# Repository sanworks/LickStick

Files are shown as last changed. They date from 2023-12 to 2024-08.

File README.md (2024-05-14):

# LickStick
A capacitive lick sensing device designed for Neuroscience research.

## Important Note ##
LickStick is in beta testing, and may still have unresolved issues.

## Contents ##
This repository includes:
* Circuit board and enclosure design files
* Link to Bill of Materials
* Firmware (Arduino language, requires Teensy board package)
* A MATLAB class to control the LickStick device

## Setup ##
* Add /LickStick/MATLAB/ to the MATLAB path
* Connect a LickStick device to your PC
* See comments in LickStick.m for usage

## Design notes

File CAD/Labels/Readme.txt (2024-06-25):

*** Screw Terminal Label Instructions ***

---Materials---
Printer: Brother PT-P900W
Label tape: TZe-S135 (12mm/0.47", White on clear, strong adhesive)

---Print settings---
Print resolution: Standard
Output: Standard
Options: Half Cut, Output Directly to Printer Driver. ALL OTHERS UNCHECKED

---Instructions---
Print labels
Cut to size on dotted lines, excluding the lines.
Peel and stick on label space above wire entry holes on wire terminal block.

*** Lickstick Logo Decal Instructions ***
Print with a die-cut sticker service.
Recommended vendor: Jukebox Print, https://www.jukeboxprint.com/ select Permanent Matte finish.

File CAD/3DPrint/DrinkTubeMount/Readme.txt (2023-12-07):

Drink tube mount designs.
v0.1 is very experimental! No results guaranteed!

Designs optimized for 3D printing.
Use FDM, with 0.4mm nozzle (e.g. Ultimaker 2+)

The mount holds a 15Ga hypodermic drink tube in place by press fit. 
The DirectContact version presses a 22ga wire onto the tube.
The FieldCoupling version places the wire adjacent to the tube with an insulating layer of plastic blocking current flow.
The mounts have a socket for a captured 4-40 nut, McMaster Part# 90730A005

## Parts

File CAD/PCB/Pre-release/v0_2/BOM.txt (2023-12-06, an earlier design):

https://docs.google.com/spreadsheets/d/1yjmNU1V_IxbT4ZvGDEUfZIvdB87yUdJNFsId-nouO-U/edit?usp=sharing

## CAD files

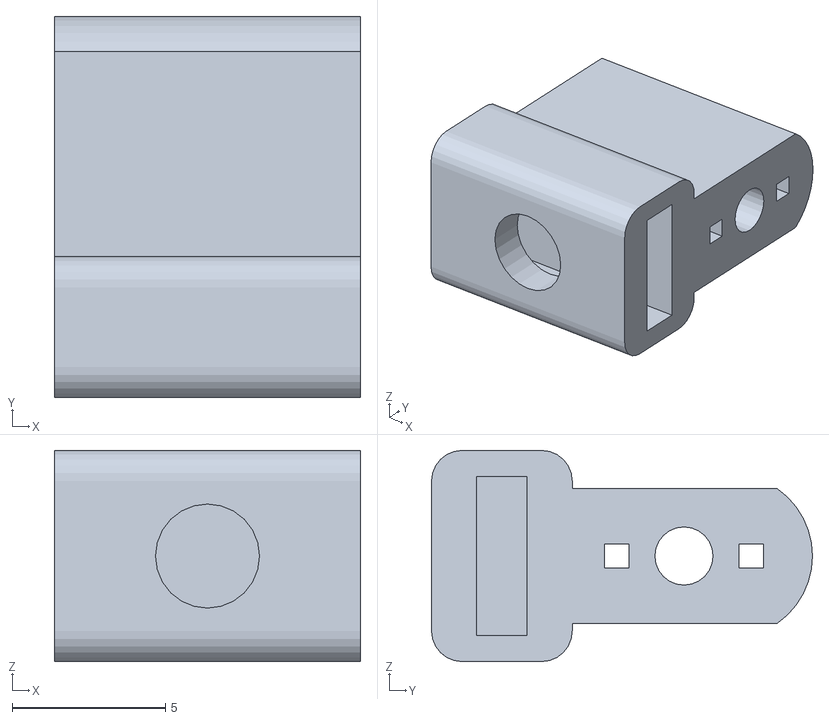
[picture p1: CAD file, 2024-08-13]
CAD/3DPrint/DrinkTubeMount/STL/LickStick_Mount_v0_2_FieldCoupling.stl
10.0 x 12.5 x 6.90

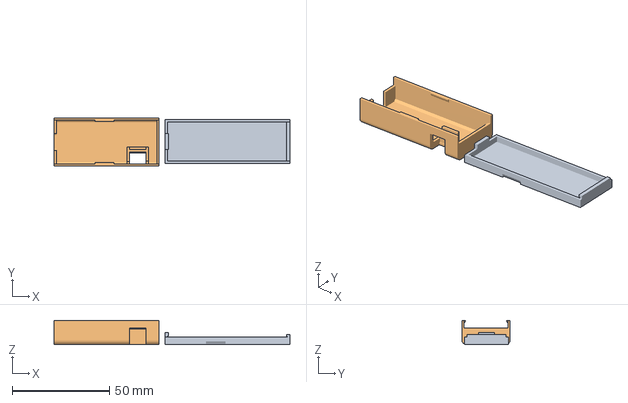
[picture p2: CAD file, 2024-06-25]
CAD/3DPrint/Enclosure/LickStick0_3_4.3mf
121.4 x 24.9 x 12.6 mm
LickStick_Enclosure_1_0_0_Bottom.stl
LickStick_Enclosure_1_0_0_Top.stl

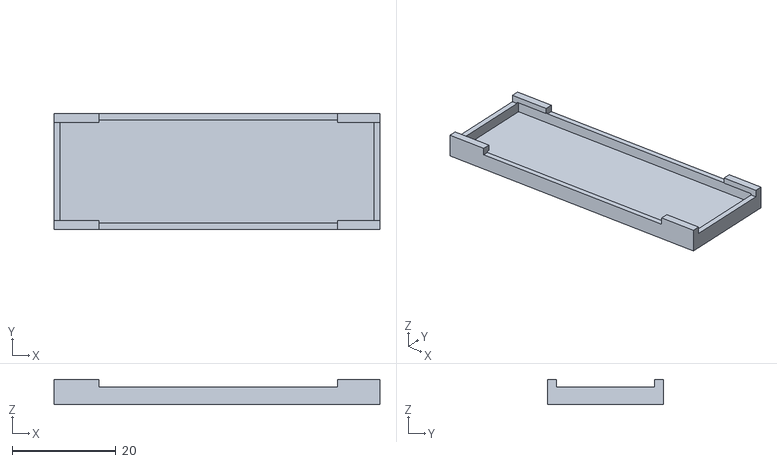
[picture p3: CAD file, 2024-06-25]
CAD/3DPrint/Enclosure/Pre-release/LickStick0_3.stl
62.8 x 22.3 x 4.85

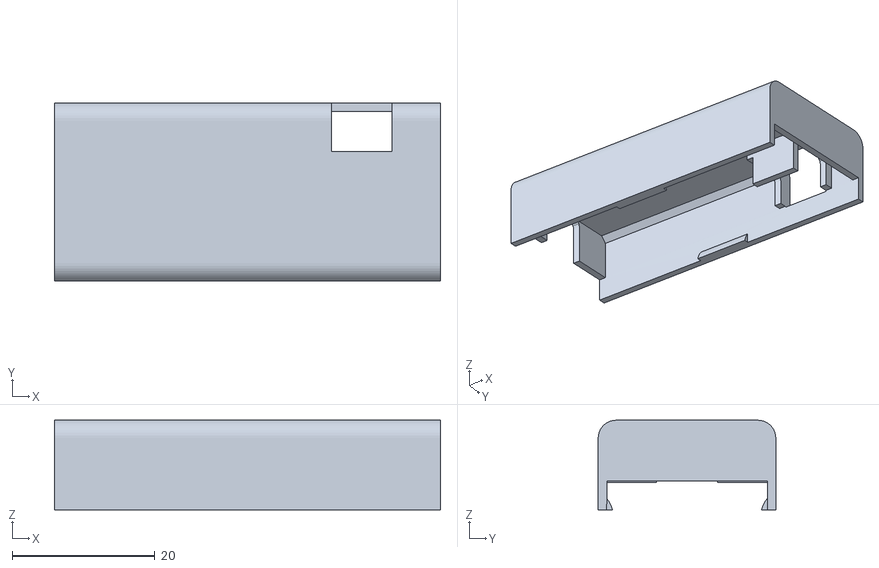
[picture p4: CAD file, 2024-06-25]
CAD/3DPrint/Enclosure/STL/LickStick_Enclosure_Top_1_0_0.stl
54.1 x 24.9 x 12.6

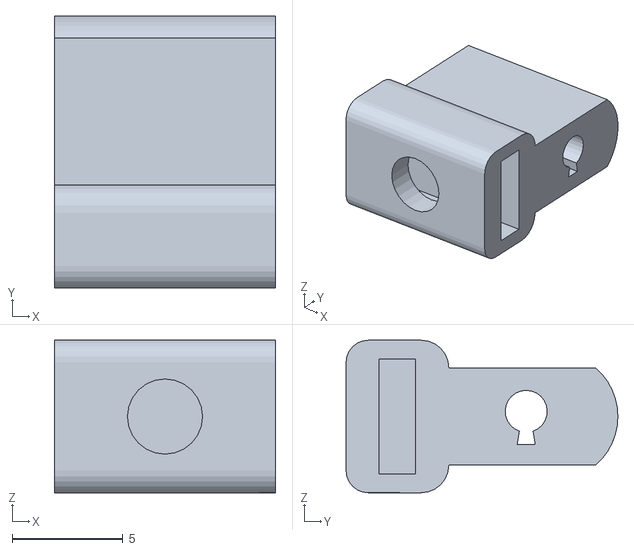
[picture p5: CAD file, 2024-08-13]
CAD/3DPrint/DrinkTubeMount/STL/LickStick_Mount_v0_2_DirectContact.stl
10.00 x 12.3 x 6.90

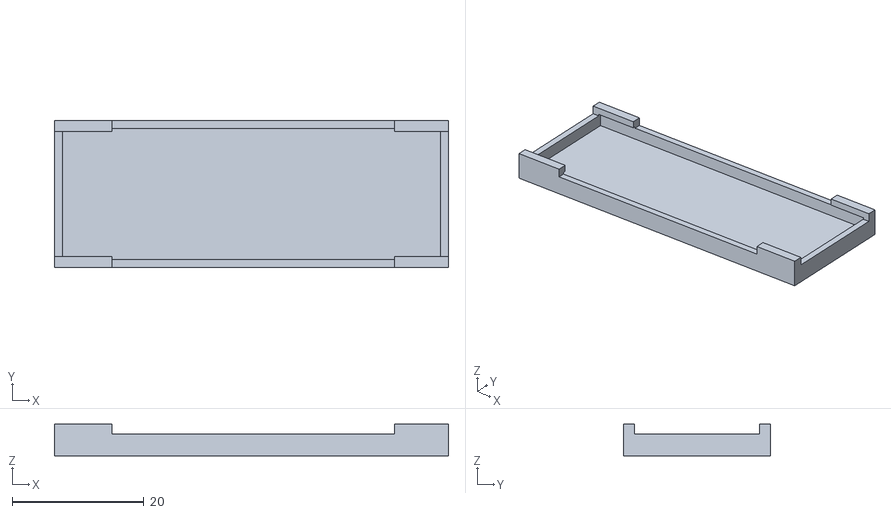
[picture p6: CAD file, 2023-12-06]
CAD/3DPrint/Enclosure/Pre-release/LickStick0_2.stl
59.8 x 22.3 x 4.85

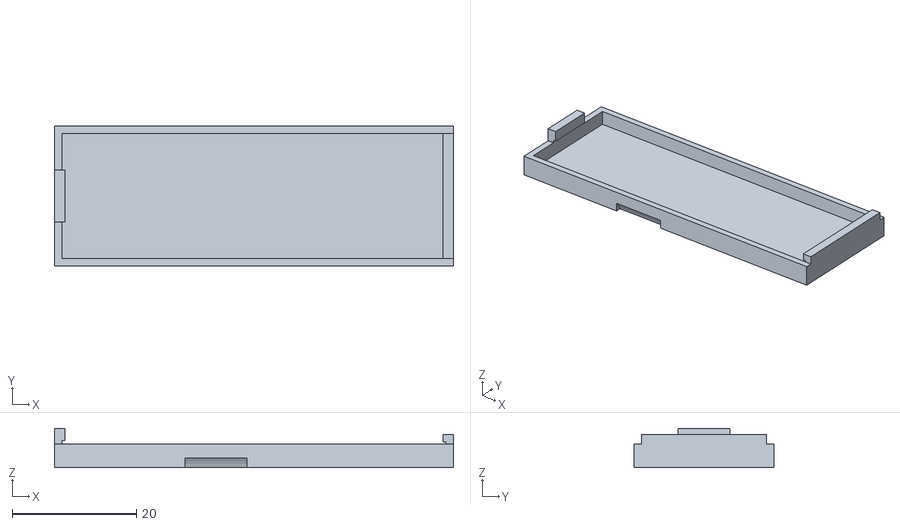
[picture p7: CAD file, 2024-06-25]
CAD/3DPrint/Enclosure/STL/LickStick_Enclosure_Bottom_1_0_0.stl
64.3 x 22.5 x 6.35

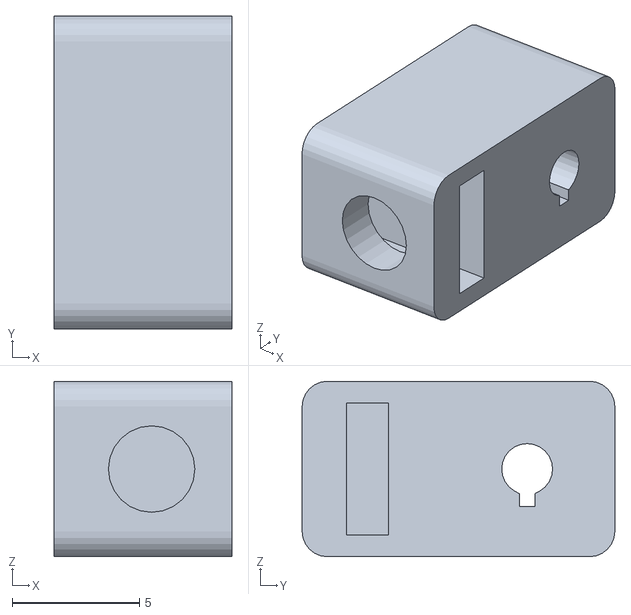
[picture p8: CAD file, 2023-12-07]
CAD/3DPrint/DrinkTubeMount/STL/LickStick_Mount_v0_1_DirectContact.stl
7.00 x 12.3 x 6.90

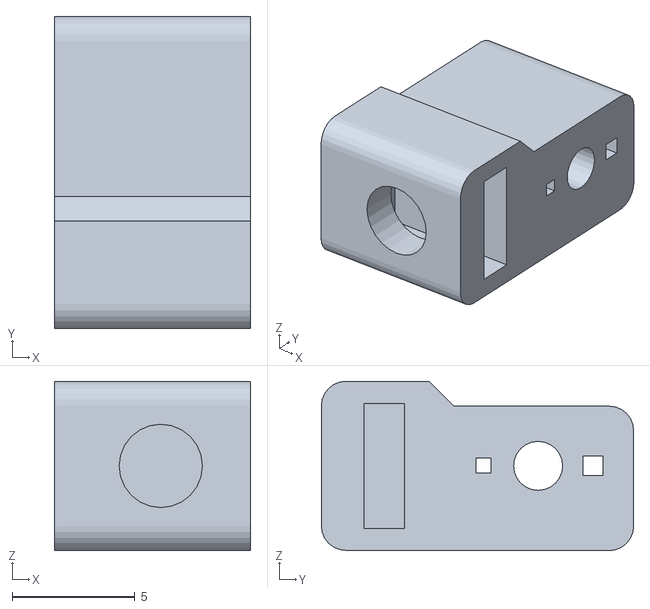
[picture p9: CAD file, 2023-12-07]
CAD/3DPrint/DrinkTubeMount/STL/LickStick_Mount_v0_1_FieldCoupling.stl
8.00 x 12.8 x 6.91

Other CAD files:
CAD/3DPrint/DrinkTubeMount/LickStick_Mount_v0_1.skp
CAD/3DPrint/DrinkTubeMount/LickStick_Mount_v0_2.skp
CAD/3DPrint/Enclosure/LickStick_Enclosure_1_0_0.skp
CAD/3DPrint/Enclosure/Pre-release/LickStick0_2.skp
CAD/3DPrint/Enclosure/Pre-release/LickStick0_3.skp
CAD/3DPrint/Enclosure/Pre-release/LickStick0_3_3.skp
CAD/3DPrint/Enclosure/Pre-release/LickStick0_3_4.skp

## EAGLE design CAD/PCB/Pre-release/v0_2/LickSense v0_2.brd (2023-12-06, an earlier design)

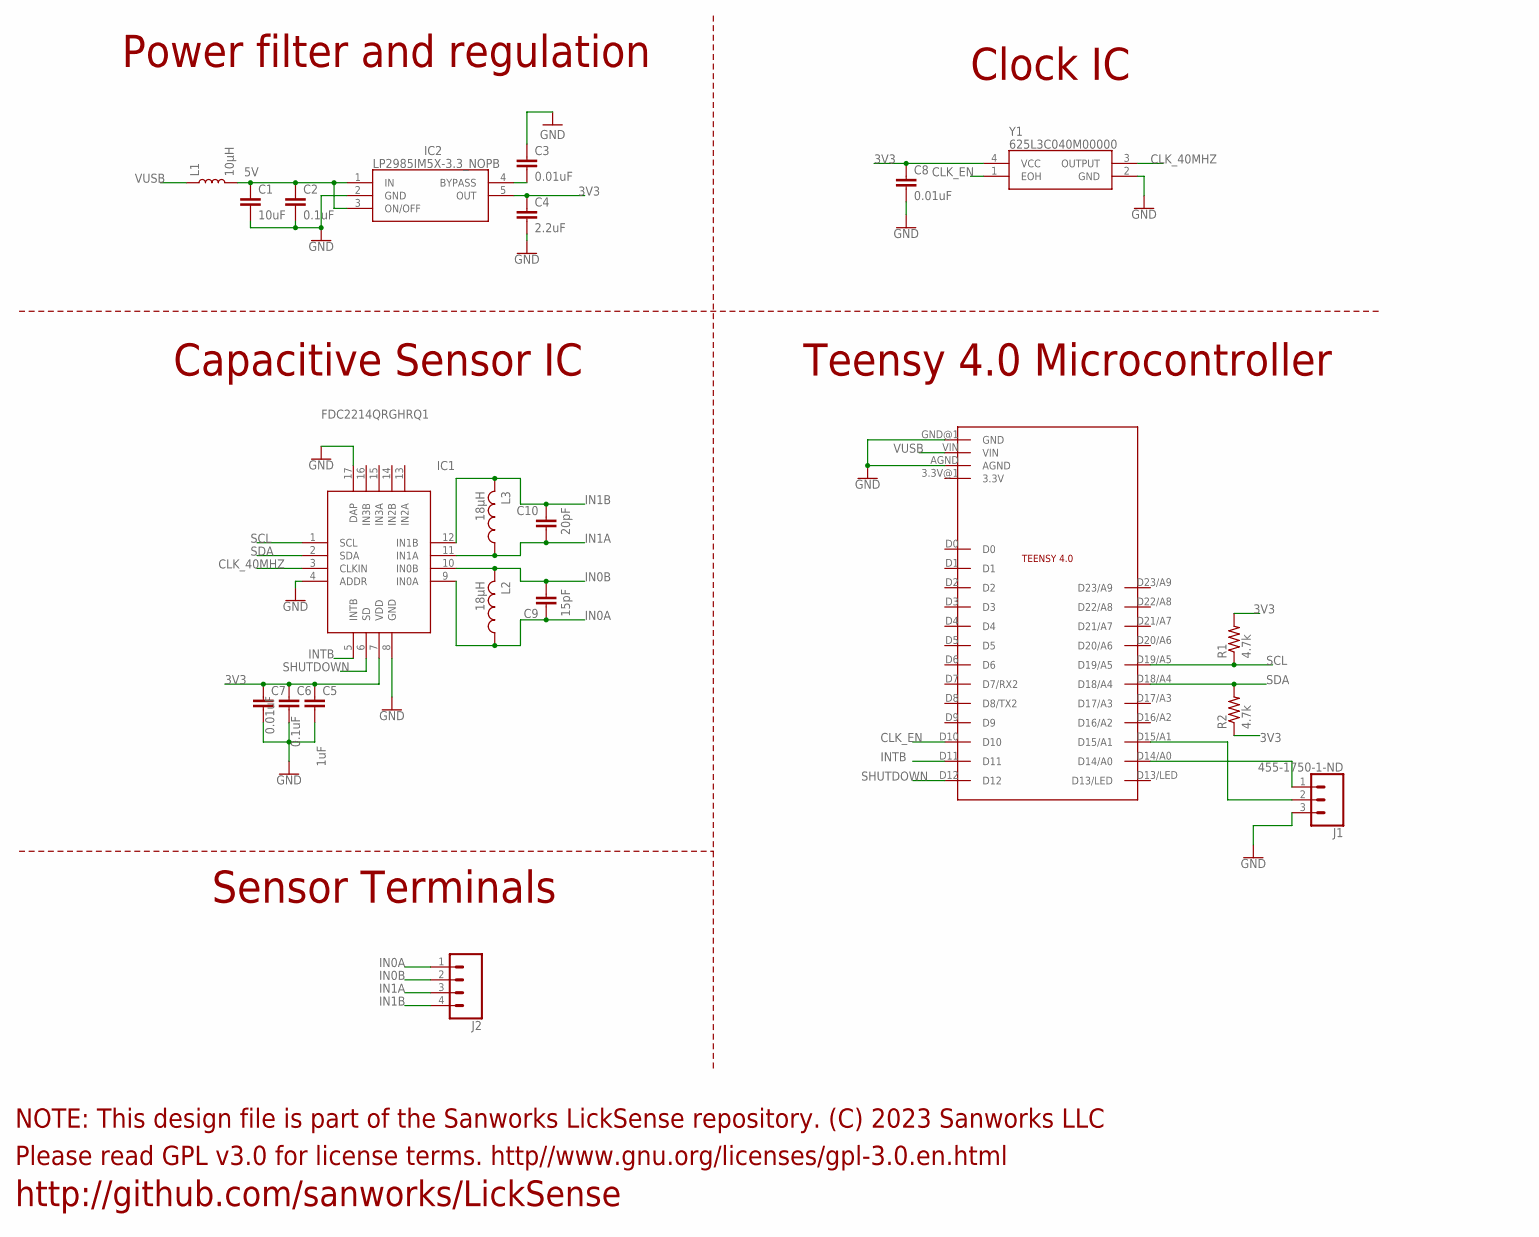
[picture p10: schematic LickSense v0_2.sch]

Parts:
C1: 10uF; 0805
C2, C6: 0.1uF; 0805
C3, C7, C8: 0.01uF; 0805
C4: 2.2uF; 0805
C5: 1uF; 0805
C9: 15pF; 0805
C10: 20pF; 0805
IC1: FDC2214QRGHRQ1; QFN50P400X400X80-17N
IC2: LP2985IM5X-3.3_NOPB; SOT95P280X145-5N
J1: 455-1750-1-ND; 1X03
J2: CONN_04PTH; 1X04
L1: 10μH; 0806
L2, L3: 18μH; L3225P
MC1: TEENSY4.0_SIMPLE_NO_VUSB
R1, R2: 4.7k; R0805
Y1: 625L3C040M00000

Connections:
3V3: C4.1, C5.1, C6.1, C7.1, C8.1, IC1.7 (VDD), IC2.5 (OUT), R1.2, R2.1, Y1.4 (VCC)
5V: C1.1, C2.1, IC2.1 (IN), IC2.3 (ON/OFF), L1.2
CLK_40MHZ: IC1.3 (CLKIN), Y1.3 (OUTPUT)
CLK_EN: MC1.D10, Y1.1 (EOH)
DIO1: J1.1, MC1.D14/A0
DIO2: J1.2, MC1.D15/A1
GND: C1.2, C2.2, C3.1, C4.2, C5.2, C6.2, C7.2, C8.2, IC1.4 (ADDR), IC1.8 (GND), IC1.17 (DAP), IC2.2 (GND), J1.3, MC1.AGND, MC1.GND@1 (GND), Y1.2 (GND)
IN0A: C9.1, IC1.9 (IN0A), J2.1, L2.1
IN0B: C9.2, IC1.10 (IN0B), J2.2, L2.2
IN1A: C10.1, IC1.11 (IN1A), J2.3, L3.1
IN1B: C10.2, IC1.12 (IN1B), J2.4, L3.2
INTB: IC1.5 (INTB), MC1.D11
unnamed: C3.2, IC2.4 (BYPASS)
SCL: IC1.1 (SCL), MC1.D19/A5, R1.1
SDA: IC1.2 (SDA), MC1.D18/A4, R2.2
SHUTDOWN: IC1.6 (SD), MC1.D12
VUSB: L1.1, MC1.VIN

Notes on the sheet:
Teensy 4.0 Microcontroller
Clock IC
Power filter and regulation
Capacitive Sensor IC
Sensor Terminals
Please read GPL v3.0 for license terms. http//www.gnu.org/licenses/gpl-3.0.en.html
NOTE: This design file is part of the Sanworks LickSense repository. (C) 2023 Sanworks LLC
http://github.com/sanworks/LickSense

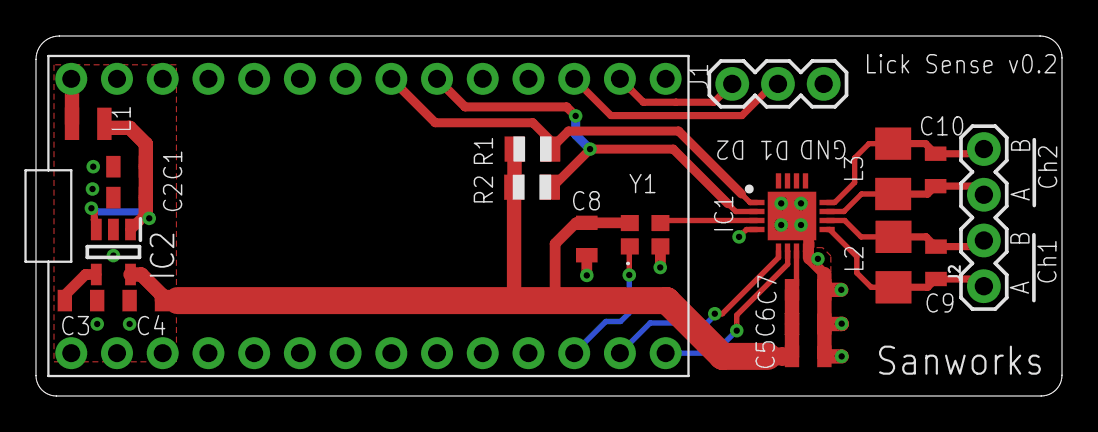
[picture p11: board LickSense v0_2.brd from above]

Board: 2 copper layers, 57.0 x 20.0 mm, 21 parts (0 on the bottom side), 17 nets.

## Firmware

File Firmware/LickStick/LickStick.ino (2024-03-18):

/*
  ----------------------------------------------------------------------------

  This file is part of the Sanworks LickSense repository
  Copyright (C) Sanworks LLC, Rochester, New York, USA

  ----------------------------------------------------------------------------

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
*/

#include <Wire.h>    // Arduino's builtin I2C class
#include "ArCOM.h"   // A wrapper to simplify transactions of different datatypes via USB serial
#include "FDC2214.h" // A class to interface with the Texas Instruments FDC2214 capacitive sensor IC

// Firmware version
#define FIRMWARE_VERSION 2

// Pin definitions
#define CLK_EN 10  // Clock enable
#define INTB 11    // Interrupt pin (configured below to report data ready)
#define SHTDWN 12  // Shutdown pin (used to reset device)
#define DIO1 15    // Digital I/O pin 1 (Middle position on green screw terminal header)
#define DIO2 14    // Digital I/O pin 2 (Right position on green screw terminal header)
#define LED_PIN 13 // LED

// Parameters
#define THRESH_DEFAULT 1900000 // Default touch detection threshold. Used from power-on until the PC connects.

// Setup interfaces
ArCOM USBCOM(Serial);
FDC2214 SensorIC(CLK_EN, INTB, SHTDWN);

// Timer used to read the sensor at even intervals
IntervalTimer readTimer;

// Program variables
byte opByte = 0;
byte inByte = 0;
byte usbStreaming = 0;
byte lickDetected = 0;
byte ledEnabled = 0;
uint16_t regValue = 0;
uint32_t thresholdValue = 0;
uint32_t nDebounceCycles = 20; // 20 cycles @ 2kHz sampling = 100Hz max licking
uint32_t debounceCounter = 0;
uint32_t nSamplesToReturn = 0;
union {
    uint8_t uint8[4];
    uint16_t uint16[2];
    uint32_t uint32[1];
} sensorValue;
union {
    byte byteArray[4];
    float floatVal;
} samplingInterval; // Hardware timer period in microseconds (500 = 2kHz). Set as a Union so it can be read as bytes.

void setup() {
  Wire.begin();
  SensorIC.init();
  pinMode(DIO1, OUTPUT);
  digitalWrite(DIO1, LOW);
  pinMode(DIO2, OUTPUT);
  digitalWrite(DIO2, LOW);
  pinMode(LED_PIN, OUTPUT);
  digitalWrite(LED_PIN, LOW);
  thresholdValue = THRESH_DEFAULT;
  samplingInterval.floatVal = 500;
  readTimer.begin(readCycle, samplingInterval.floatVal);
}

void loop() {
  if (USBCOM.available() > 0) {
    opByte = USBCOM.readByte();
    switch(opByte) {
      case 'F': // Return firmware version
        USBCOM.writeUint32(FIRMWARE_VERSION);
      break;
      case 'R': // Read sensor value
        nSamplesToReturn = USBCOM.readUint32();
        usbStreaming = 1;
      break;
      case 'S': // Start/stop USB streaming
        nSamplesToReturn = 0; // Continuous streaming
        usbStreaming = USBCOM.readByte();
      break;
      case 'W': // Set read count
        regValue = USBCOM.readUint16();
        SensorIC.set_RCOUNT(regValue);
      break;
      case 'N': // Set settle count
        regValue = USBCOM.readUint16();
        SensorIC.set_SETTLECOUNT(regValue);
      break;
      case 'D': // Set reference divider
        inByte = USBCOM.readUint8();
        SensorIC.set_REF_DIVIDER(inByte);
      break;
      case 'C': // Set drive current
        inByte = USBCOM.readUint8();
        SensorIC.set_DRIVE_CURRENT(inByte);
      break;
      case 'T': // Set threshold
        thresholdValue = USBCOM.readUint32();
      break;
      case '!': // Set active channel
        inByte = USBCOM.readByte();
        SensorIC.set_ACTIVE_CHANNEL(inByte);
      break;
      case 'I': // Set sampling interval
        USBCOM.readByteArray(samplingInterval.byteArray, 4);
        readTimer.end();
        readTimer.begin(readCycle, samplingInterval.floatVal);
      break;
      case 'L': // set LED enable/disable
        ledEnabled = USBCOM.readByte();
      break;
    }
  }
}

void readCycle() {
  sensorValue.uint32[0] = SensorIC.readSensor();
  if (debounceCounter == 0) {
    if (sensorValue.uint32[0] > thresholdValue) {
      setTTL(0);
      if (lickDetected == 1) {
        debounceCounter = nDebounceCycles;
      }
      lickDetected = 0;
    } else {
      setTTL(1);
      if (lickDetected == 0) {
        debounceCounter = nDebounceCycles;
      }
      lickDetected = 1;
    }
  } else {
    debounceCounter--;
  }
  bitWrite(sensorValue.uint8[0], 0, lickDetected); // Use LSB to encode lick detection. Bit is read and cleared on PC side
  if (usbStreaming) {
    USBCOM.writeUint32(sensorValue.uint32[0]);
    if (nSamplesToReturn > 0) {
      nSamplesToReturn--;
      if (nSamplesToReturn == 0) {
        usbStreaming = false;
      }
    }
  }
}

void setTTL(uint8_t level) {
  digitalWriteFast(DIO1, level);
  digitalWriteFast(DIO2, level);
  if (ledEnabled) {
    digitalWriteFast(LED_PIN, level);
  }
}

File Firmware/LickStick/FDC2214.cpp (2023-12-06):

/*
----------------------------------------------------------------------------

This file is part of the Sanworks repository
Copyright (C) 2023 Sanworks LLC, Rochester, New York, USA

----------------------------------------------------------------------------

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
*/

// Simplified Library for programming the FDC2214 capacitive sensor as installed on the Sanworks LickSense device


#include <Arduino.h>
#include <Wire.h>
#include "FDC2214.h"

FDC2214::FDC2214(byte clockEnable, byte intB, byte shutDown) {
  pinMode(clockEnable, OUTPUT);
  digitalWrite(clockEnable, HIGH); // Enable external clock oscillator IC
  pinMode(intB, INPUT); 
  pinMode(shutDown, OUTPUT); 
  digitalWrite(shutDown, HIGH); // Reset capacitive sensor IC
  delay(1);
  digitalWrite(shutDown, LOW);
}

void FDC2214::init() {
  Wire.begin(); // join i2c bus
  Wire.setClock(400000); // Set to I2C fast mode

  // Setup FDC2214 sensor IC
  delay(1);
  writeRegister16(REG_RESET, B10000000, B00000000); // Soft reset
  writeRegister16(REG_RCOUNT_CH0, B00000001, B00000000); // Default config: 256 ref clock cycles
  writeRegister16(REG_RCOUNT_CH1, B00000001, B00000000); 
  writeRegister16(REG_SETTLECOUNT_CH0, B00000000, B00001010); // Default config: 10 ref clock cycles
  writeRegister16(REG_SETTLECOUNT_CH1, B00000000, B00001010); 
  writeRegister16(REG_CLKDIVIDERS_CH0, B00010000, B00000001); // Default config: CH0_FIN_SEL = 2, CH0_FREF_DIVIDER = 1
  writeRegister16(REG_CLKDIVIDERS_CH1, B00010000, B00000001);
  writeRegister16(REG_ERRCONFIG, B00000000, B00000001); // Enable data-ready signal on intB pin
  writeRegister16(REG_MUXCONFIG, B00000010, B00001101); // Default config: Disable multiplexed channel sequence, sequence = [Ch0, Ch1], Deglitch filter 10MHz
  writeRegister16(REG_DRIVECURRENT_CH0, B11111000, B00000000); //Set Ch0 to maximum drive current
  writeRegister16(REG_DRIVECURRENT_CH1, B11111000, B00000000); 
  writeRegister16(REG_CONFIG, B00011110, B00000001); // MUST BE LAST - Other config regs can not be programmed while sleep mode is off! 
                                                     // Default config: Sleep mode off, configurable drive power, external clock, intB enabled, Normal current range
}

void FDC2214::sendByte(byte aByte) {
  Wire.beginTransmission(ADDRESS);
  Wire.write(aByte); 
  Wire.endTransmission();
}

void FDC2214::writeRegister16(byte regID, byte msb, byte lsb) {
  typeBuffer.uint8[0] = regID;
  typeBuffer.uint8[1] = msb;
  typeBuffer.uint8[2] = lsb;
  Wire.beginTransmission(ADDRESS);
  Wire.write(typeBuffer.uint8, 3); 
  Wire.endTransmission();
}

uint16_t FDC2214::readRegister16(byte regID) {
  sendByte(regID);
  Wire.requestFrom(ADDRESS, 2);
  typeBuffer.uint8[1] = Wire.read();
  typeBuffer.uint8[0] = Wire.read();
  return typeBuffer.uint16[0];
}

uint32_t FDC2214::readSensor() {
  uint8_t regAddress = activeChannel*2;
  sendByte(regAddress);
  Wire.requestFrom(ADDRESS, 2);
  typeBuffer.uint8[3] = Wire.read();
  typeBuffer.uint8[2] = Wire.read();
  sendByte(regAddress+1);
  Wire.requestFrom(ADDRESS, 2);
  typeBuffer.uint8[1] = Wire.read();
  typeBuffer.uint8[0] = Wire.read();
  bitClear(typeBuffer.uint8[3], 5); // Clear watchdog error bit
  bitClear(typeBuffer.uint8[3], 4); // Clear amplitude warning bit
  return typeBuffer.uint32[0];
}

void FDC2214::set_RCOUNT(uint16_t value) {
  writeRegister16(REG_CONFIG, B00111110+chConfigBit, B00000001); // Sleep
  typeBuffer.uint16[0] = value;
  writeRegister16(REG_RCOUNT_CH0, typeBuffer.uint8[1], typeBuffer.uint8[0]); // Set RCOUNT - Ch0
  writeRegister16(REG_RCOUNT_CH1, typeBuffer.uint8[1], typeBuffer.uint8[0]); // Set RCOUNT - Ch1
  writeRegister16(REG_CONFIG, B00011110+chConfigBit, B00000001); // Wakeup
}

void FDC2214::set_SETTLECOUNT(uint16_t value) {
  writeRegister16(REG_CONFIG, B00111110+chConfigBit, B00000001); // Sleep
  typeBuffer.uint16[0] = value;
  writeRegister16(REG_SETTLECOUNT_CH0, typeBuffer.uint8[1], typeBuffer.uint8[0]); // Set SETTLECOUNT - Ch0
  writeRegister16(REG_SETTLECOUNT_CH1, typeBuffer.uint8[1], typeBuffer.uint8[0]); // Set SETTLECOUNT - Ch1
  writeRegister16(REG_CONFIG, B00011110+chConfigBit, B00000001); // Wakeup
}

void FDC2214::set_REF_DIVIDER(uint8_t value) {
  writeRegister16(REG_CONFIG, B00111110+chConfigBit, B00000001); // Sleep
  writeRegister16(REG_CLKDIVIDERS_CH0, B00100000, value); // Set REF_DIVIDER - Ch0
  writeRegister16(REG_CLKDIVIDERS_CH1, B00100000, value); // Set REF_DIVIDER - Ch1
  writeRegister16(REG_CONFIG, B00011110+chConfigBit, B00000001); // Wakeup
}

void FDC2214::set_DRIVE_CURRENT(uint8_t value) {
  writeRegister16(REG_CONFIG, B00111110+chConfigBit, B00000001); // Sleep
  writeRegister16(REG_DRIVECURRENT_CH0, value << 3, B00000000); // Set DRIVECURRENT - Ch0
  writeRegister16(REG_DRIVECURRENT_CH1, value << 3, B00000000); // Set DRIVECURRENT - Ch1
  writeRegister16(REG_CONFIG, B00011110+chConfigBit, B00000001); // Wakeup
}

void FDC2214::set_ACTIVE_CHANNEL(uint8_t newChannel) {
  activeChannel = newChannel;
  chConfigBit = newChannel*B01000000;
  writeRegister16(REG_CONFIG, B00011110+chConfigBit, B00000001);  
}

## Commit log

2023-12-07 -Added MATLAB firmware loading tool, LoadLickSenseFirmware.m with compiled binaries -Added tube mount CAD files -Improved comments in LickSense.m
    [LickSense0_2.skp, LickSense0_2.stl, LickSense_Mount_v0_1.skp, LickSense_Mount_v0_1_DirectContact.stl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]
2024-05-14 -Changed project name from LickSense to LickStick -Added design files for PCB v0.3
    [LickSense v0_2.brd, LickSense v0_2.sch, LickStick v0_3.brd, LickStick v0_3.sch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]
2024-06-25 -Added PCB v1.0.1 -Added enclosure v1.0 -MATLAB: Modded activeChannel numbers to match labels on device
    [LickSense v0_2.brd, LickSense v0_2.sch, LickStick v0_3.brd, LickStick v0_3.sch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]
2024-08-13 -Added STL for drink tube mount v0.2
    [LickStick_Mount_v0_2_DirectContact.stl, LickStick_Mount_v0_2_FieldCoupling.stl]
2024-11-01 -MATLAB GUI: Added pushbuttons to increase/decrease threshold
    [LickStick_Mount_v0_2.skp]

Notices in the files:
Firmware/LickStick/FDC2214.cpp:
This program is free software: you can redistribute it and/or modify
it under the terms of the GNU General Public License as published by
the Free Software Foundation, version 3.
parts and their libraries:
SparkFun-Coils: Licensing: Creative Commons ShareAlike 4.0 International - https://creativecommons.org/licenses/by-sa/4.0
